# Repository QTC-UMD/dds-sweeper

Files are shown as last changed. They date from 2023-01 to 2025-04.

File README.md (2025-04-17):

# dds-sweeper

Raspberry Pi Pico interface for the AD9959 DDS.

If you use this project, please cite as:

E. Huegler, J. C. Hill, and D. H. Meyer, An agile radio-frequency source using internal sweeps of a direct digital synthesizer,
*Review of Scientific Instruments*, **94**, 094705 (2023)
[https://doi.org/10.1063/5.0163342](https://doi.org/10.1063/5.0163342)

## Specs

- The timing capabilities of the DDS-Sweeper are tied to the number of clock cycles the pico takes to send the next instruction.  

| Table Mode      | 1 Channel | 2 Channel | 3 Channel | 4 Channel |
|-----------------|-----------|-----------|-----------|-----------|
| Single Stepping | 500       | 750       | 1000      | 1250      |
| Sweep Mode      | 1000      | 1500      | 2000      | 2500      |

- At the default Pico Clock frequency of 125 MHz those clock cycle counts correspond to the following times:  

| Table Mode      | 1 Channel | 2 Channel  | 3 Channel  | 4 Channel  |
|-----------------|-----------|------------|------------|------------|
| Single Stepping | 4 $\mu s$ | 6  $\mu s$ | 8  $\mu s$ | 10 $\mu s$ |
| Sweep Mode      | 8 $\mu s$ | 12 $\mu s$ | 16 $\mu s$ | 20 $\mu s$ |

- The number of instructions you can store in the table depends on the type of sweep being performed, the number of channels being used, and the pico chip version. We allocated a maximum ram size of:

244 kB (RP 2040):

| Table Mode                  | 1 Channel | 2 Channel | 3 Channel | 4 Channel |
|-----------------------------|-----------|-----------|-----------|-----------|
| Single Stepping (Ext Timer) | 16656     | 8615      | 5810      | 4383      |
| Sweep Mode (Ext Timer)      | 8614      | 4382      | 2938      | 2210      |
| Single Stepping (Int Timer) | 5000      | 5000      | 5000      | 4032      |
| Sweep Mode (Int Timer)      | 5000      | 4032      | 2703      | 2033      |

500 kB (RP 2350):

| Table Mode                  | 1 Channel | 2 Channel | 3 Channel | 4 Channel |
|-----------------------------|-----------|-----------|-----------|-----------|
| Single Stepping (Ext Timer) | 34132     | 17654     | 11905     | 8981      |
| Sweep Mode (Ext Timer)      | 17654     | 8981      | 6022      | 4529      |
| Single Stepping (Int Timer) | 5000      | 5000      | 5000      | 5000      |
| Sweep Mode (Int Timer)      | 5000      | 5000      | 5000      | 4353      |

## How to flash the firmware

Download the latest [dds-sweeper.uf2 file](https://github.com/QTC-UMD/dds-sweeper/releases/latest/download/dds-sweeper.uf2).
On your Raspberry Pi Pico, hold down the "bootsel" button while plugging the Pico into USB port on a PC (that must already be turned on).
The Pico should mount as a mass storage device (if it doesn't, try again or consult the Pico documentation).
Drag and drop the `.uf2` file into the mounted mass storage device.
The mass storage device should unmount after the copy completes. Your Pico is now running the DDS Sweeper firmware!

## Usage

### Setup

When the DDS Sweeper is started, configuration is required before it can be used. It is often good to begin with a `reset` command, which resets the AD9959.

First, the clock should be setup with the `setclock` command, followed by the `setmult` command.

Second, the number of channels should be configured with the `setchannels` command.

Finally, the mode and timing should be setup with the `mode` command. The DDS Sweeper uses either discrete amplitude, frequency, and phase steps or sweeps of one parameter (possibly with steps of the other parameter) as its primitive instructions. The DDS Sweeper can then use internal timing (in which case it generates triggers internally after each step or sweep) or external timing (in which case it waits for external triggers).

### Program loading

Once setup is complete, instructions (steps or sweeps, depending on the mode) and timings can be loaded using the `set`, `seti`, or `setb` commands. In addition to output instructions, there are special stop and repeat instructions (which can only be loaded using `seti` and `setb`). With instructions are loaded, the address (order in which they are executed) is specified, so the order of loading need not match the order of execution. Timing is set per address, so it is common to all channels. The stop instruction ends program execution, while the repeat instruction restarts program execution from the beginning. Instructions are loaded into an uninitialized array, so skipping instruction addresses or failing to specify stop/repeat at the end of the program may result in undefined behavior.

### Execution

Finally, the program can be executed using the `start` or `hwstart` commands. If termination of the program is required before it reaches a `stop` command, the `abort` command can be used.

## DDS Units

- Output Amplitude is dependent on frequency (some people on Analog Devices forum mentioned amplitude and frequency are related by a sinc function)

- The frequency resolution of the AD9959 is $= \frac{f_{sys clk}}{2^{32}}$. At the default system clock of 500 MHz, the frequency resolution is $\approx 0.1164$ Hz. Frequency input to the DDS Sweeper using the `set` command will be rounded to an integer multiple of the frequency resolution. Frequency input to the DDS Sweeper using the `seti` or `setb` commands will be in units of the frequency resolution.

- The phase resolution of the AD9959 is $= \frac{360^\circ}{2^{14}} \approx 0.02197^\circ$. Phase offsets given using the `set` command will be rounded to a multiple of this resolution. Phase offsets given using the `seti` or `setb` commands will be in units of this resolution.

- The amplitude resolution of the AD9959 is $= \frac{1}{2^{10}} \approx 0.09767\%$. Amplitude scale factors given using the `set` command will be rounded to a multiple of this resolution. Amplitude scale factors given using the `seti` or `setb` commands will be in units of this resolution.

- When the DDS Sweeper uses internal timing to execute instructions, that time is based on the number of clock cycles of the Pico's system clock (which defaults to 125 MHz for an 8 ns period). Timing inputs using the `set` command are given in seconds and will be rounded to an integer multiple of the Pico system clock period. Timing input using the `seti` or `setb` commands is defined to be in units of the Pico system clock period.

## Sweeps

- Setting up a sweep:  
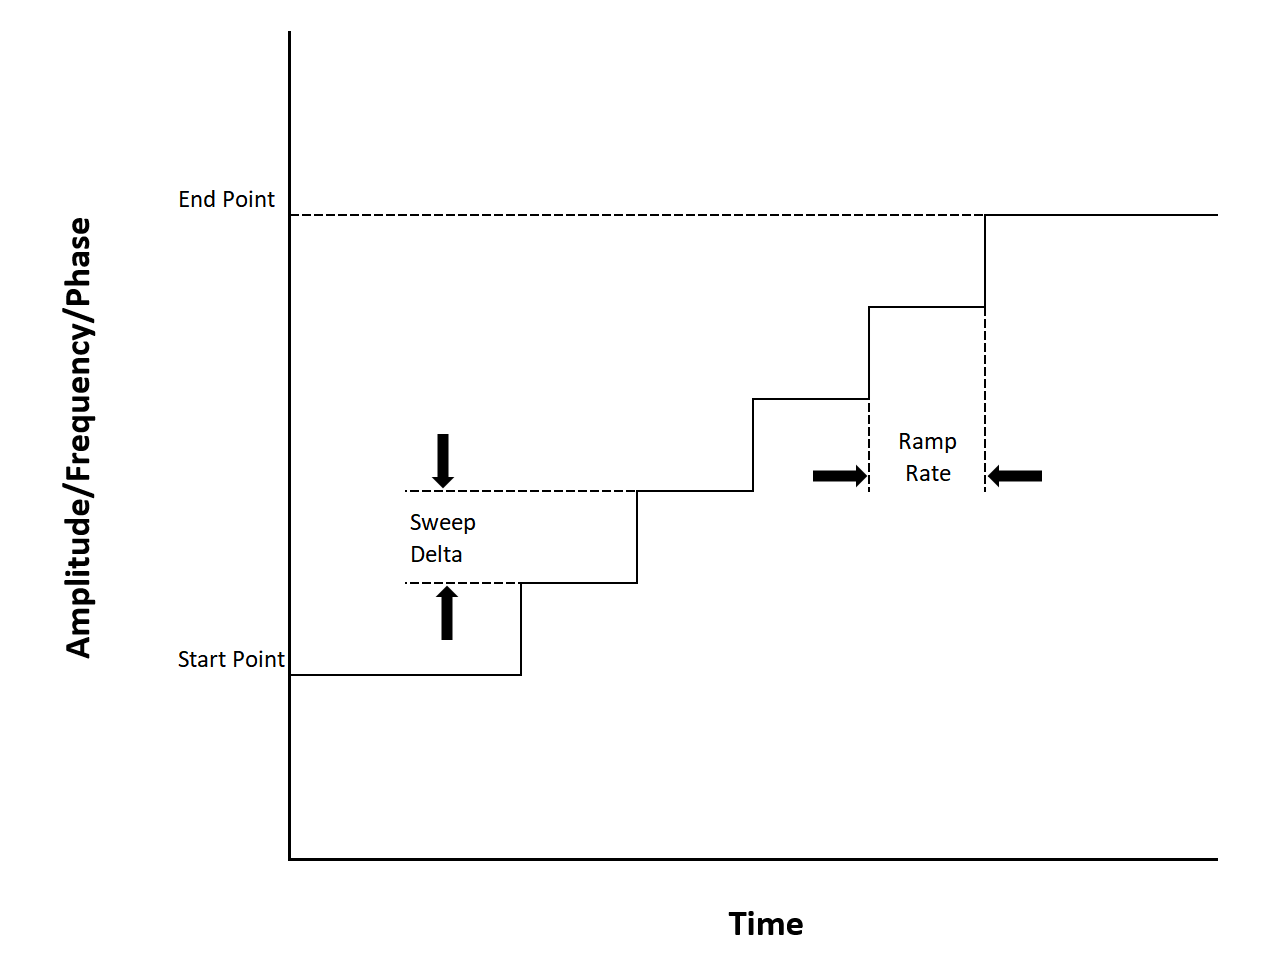
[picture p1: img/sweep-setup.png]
Sweep Setup Figure
  
Sweeps are defined by two parameters, sweep delta and ramp rate.
- Sweep Delta defines the change in output amplitude/frequency/phase on each sweep step
- Ramp rate defines how often a sweep step is taken. It is based off of the AD9959's sync clock signal which will be one quarter of the AD9959's system clock. The ramp rate parameter specifies the number of sync clock cycles per sweep step. A ramp rate of 1 will cause the sweep delta to be applied every 1 sync clock cycle. For upward sweeps, the ramp rate parameter can have a value of 1-255. For downward sweeps the ramp rate can only be 1.  

For more details on sweeps, see [sweep details](SWEEP_DETAILS.md).

## Serial API

Note: Commands must be terminated with `\n`.

### Status commands

- `version`:  
Responds with a string containing the firmware version.

- `status`:  
Returns the operating status of the DDS-Sweeper.

  - `0`: manual mode
  - `1`: transitioning to buffered execution
  - `2`: buffered execution
  - `3`: aborting buffered execution
  - `4`: last buffered execution was aborted
  - `5`: transitioning to manual mode

- `clkstatus`:
Returns the clocking status of the DDS-Sweeper as three numbers: `<int:mode> <double:freq> <int:mult>`.
Mode can be `0` for internal clocking or `1` for external clocking of the AD9959.
The frequency is the AD9959 reference frequency, in Hz.
`mult` is the AD9959 PLL multiplier. The corresponding system frequency is `freq*-*mult`.

- `board`:
Responds with which type of board the firmware is running on: `pico1` or `pico2`.

- `getfreqs`:  
Responds with a multi-line string containing the current operating frequencies of various clocks (you will be most interested in `pll_sys` and `clk_sys`). Multiline string ends with `ok\n`.

### State commands

- `start`:  
Starts buffered execution immediately.

- `hwstart`:  
Starts buffered execution once an external trigger is received.

- `abort`:  
Stops buffered execution immediately.

### Setup commands

- `setclock <mode:int> <freq:int> (<pll_mult:int>)`:  
Reconfigures the source/reference clock.
  - Mode `0`: Use pico system clock as reference to the AD9959.
    In this mode, the frequency provided also sets the pico system clock
    and it cannot exceed 133 MHz.
    The dds sweeper defaults to this mode with a frequency of 125 MHz and a PLL multiplier of 4.
  - Mode `1`: Sets the AD9959 to receive a reference clock not from the pico.
    Setting this mode does not change the pico system clock.

  `pll_mult` is an optional input that sets the AD9959's PLL multiplier on the Reference Clock input. The default value is 4, giving the AD9959 a system clock of 500 MHz with the pico's 125 MHz reference. Valid values are 1 or 4-20.  
  The AD9959's PLL has an output range of 100-160 MHz or 255-500 MHz with VCO gain enabled. The pico will automatically enable the VCO gain bit if the requested frequency is in the upper range. If trying to use the PLL multiplier to generate a frequency between 160 and 255 MHz, there is no guarantee of operation.

- `setchannels <num:int>`:  
Sets how many channels being used by the table mode. Uses the lowest channels first, starting with channel 0. If number of channels is set to `0`, buffered execution instructions will be written to all 4 channels simultaneously.

- `mode <sweep-type:int> <trigger-source:int>`:  
Configures what mode the DDS-Sweeper is operating in
  - 0: single stepping / manual mode
  - 1: amplitude sweep
  - 2: frequency sweep
  - 3: phase sweep
  - 4: amplitude sweep with frequency/phase steps
  - 5: frequency sweep with amplitude/phase steps
  - 6: phase sweep with frequency/amplitude steps  

  The operating mode must be set before buffered execution instructions can be programmed into the DDS-Sweeper.  
  A `trigger-source` of `0` means the Sweeper is expecting external triggers. A `trigger-source` of `1` means the Sweeper will send its own triggers and `set` commands will require an additional `time` argument.

### Manual output commands

- `setfreq <channel:int> <frequency:float>`:  
Manually set the output frequency of a specified channel. Channels are 0-3 and frequencies are in Hz. If `debug` is set to on, it will respond with the actual frequency set. The Sweeper must be in manual mode.

- `setphase <channel:int> <phase_offset:float>`:  
Manually set the phase offset of a specified channel. Channels are 0-3 and offsets are in degrees. If `debug` is set to on, it will respond with the actual degree offset set. The Sweeper must be in manual mode.

- `setamp <channel:int> <amplitude_scale_factor:float>`:  
Manually set the amplitude scale factor of a specified channel. Channels are 0-3 and amplitude scale factors are a precentage of the maximum output voltage. If `debug` is set to on, it will respond with the actual frequency set. The Sweeper must be in manual mode.

### Data loading commands

- `set`:  
Sets the value of instruction number `addr` for channel `channel` (zero indexed). `addr` starts at 0. It looks different depending on what mode the sweeper is in. If `Debug` is set to `on` it will respond with the actual values set for that instruction.
  - Single Stepping (mode 0): `set <channel:int> <addr:int> <frequency:float> <amplitude:float> <phase:float> (<time:float>)`
  - Sweep Mode (modes 1-3): `set <channel:int> <addr:int> <start_point:float> <end_point:float> <sweep_rate:float> (<time:float>)`

    `start_point` is the value the sweep should start from, and `end_point` is where it will stop. `sweep_rate` is the amount that the output should change in each quantity's units per second (further info below). In the AD9959, the sweep clock runs at one quarter the system clock. The types of values expected for `start_point`, `end_point`, and `sweep_rate` are different depending on the type of sweep:  
    - Amplitude Sweeps (mode 1)  
      `start_point` and `end_point` should be decimals between 0 and 1 that represent the desired proportion of the maximum output amplitude. `sweep_rate` is then that proportion per second. The resolution of the start and end values is $\frac{1}{1024} \approx 0.09766$.
    - Frequency Sweeps (mode 2)  
      `start_point` and `end_point` are frequencies in Hz, with `sweep_rate` in Hz per second. The start and end points can have decimal values, but they will be rounded to the nearest multiple of the frequency resolution ($\frac{f_{sysclk}}{2^{32}}$).
    - Phase Sweeps (mode 3)
      `start_point`, `end_point` are in degrees, with `sweep_rate` in degrees per second. The start and end points can have decimal values, but they will be rounded to the nearest multiple of the phase resolution ($\frac{360^\circ}{2^{14}} \approx 0.02197^\circ$).

  - Sweep and Single Stepping Mode (modes 4-6): `set <channel:int> <addr:int> <start_point:float> <end_point:float> <sweep_rate:float> <secondary1:double> <secondary2:double> (<time:float>)`

  These modes perform a linear sweep on one of the parameters, while simultaneously single stepping on the other two parameters.
  - Amplitude Sweeps (mode 4)  
    `secondary1` is the frequency, and `secondary2` is the phase offset.
  - Frequency Sweeps (mode 5)  
    `secondary1` is the amplitude scale factor, and `secondary2` is the phase offset.
  - Phase Sweeps (mode 6)  
    `secondary1` is the frequency, and `secondary2` is the amplitude scale factor.

- `seti`:  
Sets the value of instruction number `addr` for channel `channel` (zero indexed). `addr` starts at 0. It looks different depending on what mode the sweeper is in. If `Debug` is set to `on` it will respond with the actual values set for that instruction. `seti` uses integer values (AD9959 units) rather than floating point values. Otherwise, it is the same as `set`.
  - Single Stepping (mode 0): `seti <channel:int> <addr:int> <frequency:int> <amplitude:int> <phase:int> (<time:int>)`
  - Sweep Mode (modes 1-3): `seti <channel:int> <addr:int> <start_point:int> <end_point:int> <delta:int> <ramp-rate:int> (<time:int>)`

    `start_point` is the value the sweep should start from, and `end_point` is where it will stop. `delta` is the amount that the output should change by every cycle of the sweep clock. In the AD9959, the sweep clock runs at one quarter the system clock. `ramp-rate` is an additional divider that can applied to slow down the sweep clock further, must be in the range 1-255. The types of values expected for `start_point`, `end_point`, and `delta` different depending on the type of sweep  
    - Amplitude Sweeps (mode 1)  
      `start_point` and `end_point` should be integers between 0 and 1023 (inclusive).
    - Frequency Sweeps (mode 2)  
      `start_point`, `end_point`, and `delta` are integers between 0 and $2^{32} - 1$ in units of system clock rate (typically $500$ MHz) over $2^{32}$.
    - Phase Sweeps (mode 3)
      `start_point`, `end_point`, and `delta` are between 0 and 65535 (inclusive).

  - Sweep and Single Stepping Mode (modes 4-6): `set <channel:int> <addr:int> <start_point:int> <end_point:int> <delta:int> <ramp-rate:int> <secondary1:int> <secondary2:int> (<time:int>)`

    These modes perform a linear sweep on one of the parameters, while simultaneously single stepping on the other two parameters.
    - Amplitude Sweeps (mode 4)  
      `secondary1` is the frequency, and `secondary2` is the phase offset.
    - Frequency Sweeps (mode 5)  
      `secondary1` is the amplitude scale factor, and `secondary2` is the phase offset.
    - Phase Sweeps (mode 6)  
      `secondary1` is the frequency, and `secondary2` is the amplitude scale factor.

- `setb <start address:int> <instruction count:int>`:  
Bulk setting of instructions in binary. `start address` is the address of the first instruction loaded. `instruction count` instructions will be programmed. If there is not sufficient space for that many instructions, the response will be an error message. Otherwise, the response will be `ready for <byte count:int> bytes`, where `byte count` is the number of bytes the device is expecting. An array of instructions can then be transmitted. Note that all active channels are loaded together. The layout of the instruction array is mode dependent, and in the table below each mode is assumed to use external timing (where internal timing bytes are in parentheses and the dtype list must have `, ('time', '<u4')` appended)

| Mode  | Bytes per channel per instruction  | np.dtype  |
|---| :---: |:---:|
| Single Stepping (mode 0)  | 8 (12) | `[('frequency', '<u4'), ('amplitude', '<u2'), ('phase', '<u2')]`  |
| Amplitude Sweeps (mode 1)  | 7 (11) |  `[('start_amplitude', '<u2'), ('stop_amplitude', '<u2'), ('delta', '<u2'), ('rate', '<u1')]` |
| Frequency Sweeps (mode 2) | 13 (17) |  `[('start_frequency', '<u4'), ('stop_frequency', '<u4'), ('delta', '<u4'), ('rate', '<u1')]` |
| Phase Sweeps (mode 3)  | 7 (11) | `[('start_phase', '<u2'), ('stop_phase', '<u2'), ('delta', '<u2'), ('rate', '<u1')]` |
| Amplitude Sweep and Single Stepping (mode 4) | 13 (17)  | `[('start_amplitude', '<u2'), ('stop_amplitude', '<u2'), ('delta', '<u2'), ('rate', '<u1'), ('frequency', '<u4'), ('phase', '<u2')]`  |
| Frequency Sweep and Single Stepping (mode 5) | 17 (21) | `[('start_frequency', '<u4'), ('stop_frequency', '<u4'), ('delta', '<u4'), ('rate', '<u1'), ('amplitude', '<u2'), ('phase', '<u2')]`  |
| Phase Sweep and Single Stepping (mode 6)  | 13 (17) | `[('start_phase', '<u2'), ('stop_phase', '<u2'), ('delta', '<u2'), ('rate', '<u1'), ('frequency', '<u4'), ('amplitude', '<u2')]`  |

### Flash commands

- `save`:  
Saves the buffered execution table to nonvolatile memory so that it can be recovered later (after a power cycle).

- `load`:  
Retrieves the buffered execution table stored in nonvolatile memory and restores it to system memory so that it can be run. A saved table must be loaded before it can be run.

### Debugging commands

- `debug <state:str>`:  
Turns on extra debug messages printed over serial. `state` should be `on` or `off` (no string quotes required). On by default.

- `numtriggers`:  
Responds with the number of triggers processed since the last call of `start`

- `program`:  
Reboots the Pi Pico into firmware flashing mode. Serial will immediately disconnect and a mass storage device should appear.

## Compiling the firmware

If you want to make changes to the firmware, or want to compile it yourself (because you don't trust binary blobs from the internet), we provide a docker configuration to help you do that.

1. Install docker desktop and make sure it is running (if you are on Windows, you may have to mess around a bit to get virtualisation working at an operating system level)
2. Clone this repository
3. Open a terminal with the current working directory set to the repository root (the `docker-compose.yaml`` file should be there)
4. Run `docker compose build --pull` to build the docker container
5. Run `docker compose up` to build the PrawnBlaster firmware.

Step 4 will take a while as it has to build the docker container.
If it is slow to download packages from the Ubuntu package repositories, consider providing an explicit apt mirror that is fast for you: `docker compose build --pull --build-arg APT_MIRROR="http://azure.archive.ubuntu.com/ubuntu/"`.

If you want to change which version of the pico SDK it builds against, this is set in the `build/docker/Dockerfile` file.
Just change the git tag of the pico SDK that gets cloned out by git, then rebuild the docker container (see step 4).

Note once the docker container is built, you can run step 5 as many times as you like.
You do not need to rebuild the container, even if you make changes to the PrawnBlaster source code.
You only need to rebuild the docker container if you modify the `build/docker/Dockerfile` file.

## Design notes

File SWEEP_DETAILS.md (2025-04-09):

# Sweeps

- Setting up a sweep:  
Sweep Setup Figure  
Sweeps are defined by two parameters, sweep delta and ramp rate.
- Sweep Delta defines the change in output amplitude/frequency/phase on each sweep step.
- Ramp rate defines how often a sweep step is taken. It is based off of the AD9959's sync clock signal which will be one quarter of the AD9959's system clock. The ramp rate parameter specifies the number of sync clock cycles per sweep step. A ramp rate of 1 will cause the sweep delta to be applied every 1 sync clock cycle. For upward sweeps, the ramp rate parameter can have a value of 1-255. For downward sweeps the ramp rate can only be 1.  

The time between sweep steps can be calculated with:
$ t = \frac{\textrm{Ramp Rate}}{\textrm{Sync Clock}} $
Using the Pico's 125 Mhz with a 4 times PLL Multiplier gives the AD9959 a system clock of 500 MHz and therefore a sync clock of 125 MHz.
For upward sweeps the time between sweeps can range from $\frac{1}{125 MHz} = 8 ns$ to $\frac{255}{125 MHz} = 2.04 \mu s$.
Downward sweeps will apply the sweep delta every $\frac{1}{125 MHz} = 8 ns$.  
Given the frequency resolution of $\frac{f_{sys clk}}{2^{32}}$, the smallest sweep delta is $\frac{1}{2^{32}} = 0.1164$ Hz. With the maximum ramp rates, the DDS-sweeper has a minimum sweeping rate of $\approx 47871$ Hz/sec when sweeping upwards or $\approx 12207031.25$ Hz/sec when sweeping downward.

## Finer Sweep Rate Resolution in `set`

The `set` command will internally calculate the sweep delta and ramp rate by given the user provided `sweep_rate` using the continued fraction algorithm. Given a conversion factor $B$ that allows us to convert a sweep rate $R$ to bits per sync clock cycle,  

$$B_{freq} = \frac{2^{32}}{f_{sysclk}} [\frac{\text{bits}}{\text{Hz}}], B_{amp} = 2^{10} [\frac{\text{bits}}{\text{Arb.}}], B_{phase} = 2^{14}[\frac{\text{bits}}{\text{degree}}],$$

the ratio of sweep delta $d$ and ramp rate $r$ can be equated to the following:  

$$
\frac{d}{r} = B\frac{4R}{f_{sysclk}}
$$.

The continued fraction algorithm then returns the integer ratio approximation of the desired `sweep_rate` float and therefore set an integer sweep delta and ramp rate. The algorithm will respect the limits of each sweep mode, so the frequency tuning word sweep deltas can be between $0$ and $2^{32}-1$, amplitude scale factor sweep deltas can be between $0$ and $2^{10}$, and phase offset word sweep deltas can be between $0$ and $2^{14}$. The ramp rates for each mode are constrained to be between $1$ and $255$ for upward sweeps, and held to $1$ for downward sweeps.

## Downward Sweeps

Downward sweeps are not well supported by the AD9959, but they can still be done.
The best method I have found for doing a downward sweep is to send the instructions via serial first, with the sweep autoclear bit set to active and the rising sweep tuning word set to the maximum.
Then issue the IO_UPDATE signal while keeping the profile pin for that channel high.
I believe this clears the sweep accumulator then quickly refills it with a max rate sweep before beginning the downward sweep.
Other combinations of autoclear bit active or not and timing of the profile pins seem to cause even more issues with downward sweeps.
The biggest downside of this method is that you cannot slow down the downward sweep ramp rate as much as the upward sweep ramp rate.

- Autoclear Accumulator Active, drop the pin after the update:  
  Seems to work, you just cannot slow down downward sweeps.
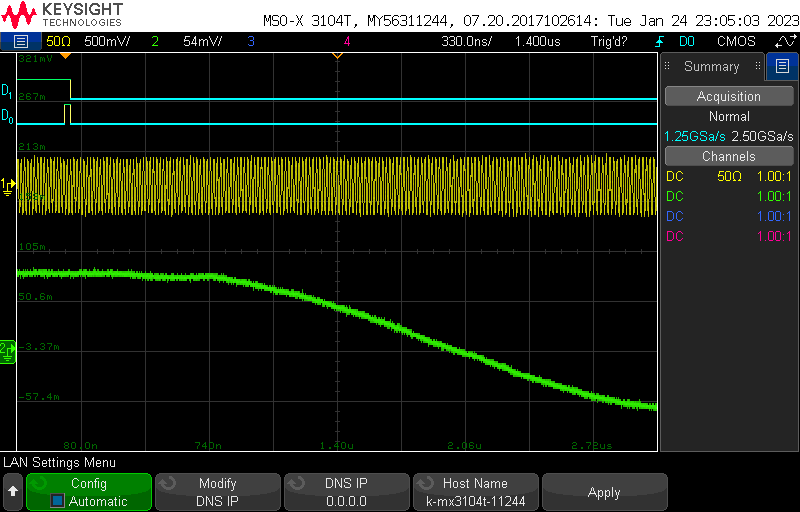
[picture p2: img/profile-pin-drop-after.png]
Autoclear Accumulator Active, drop the pin after the update Closeup
    
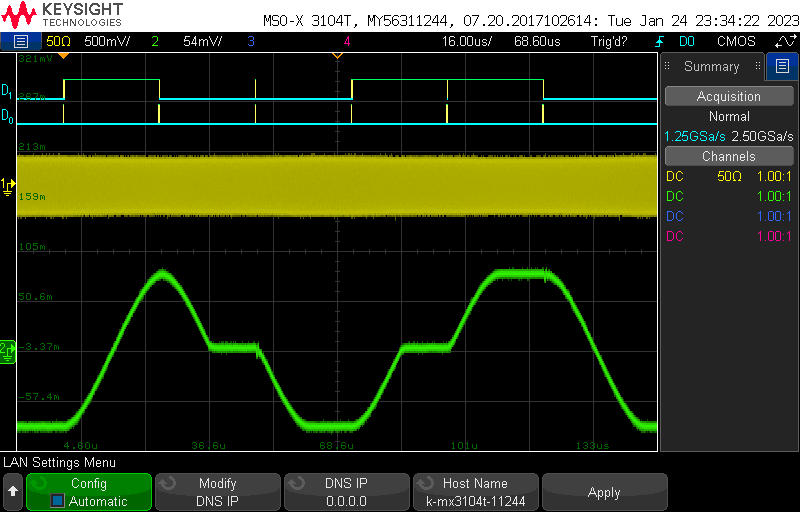
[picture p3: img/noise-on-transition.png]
Autoclear Accumulator Active, drop the pin after the update Multiple Sweeps
  

- Autoclear Accumulator Active, drop the pin before the update:  
  Downward sweeps just dont work at all.  
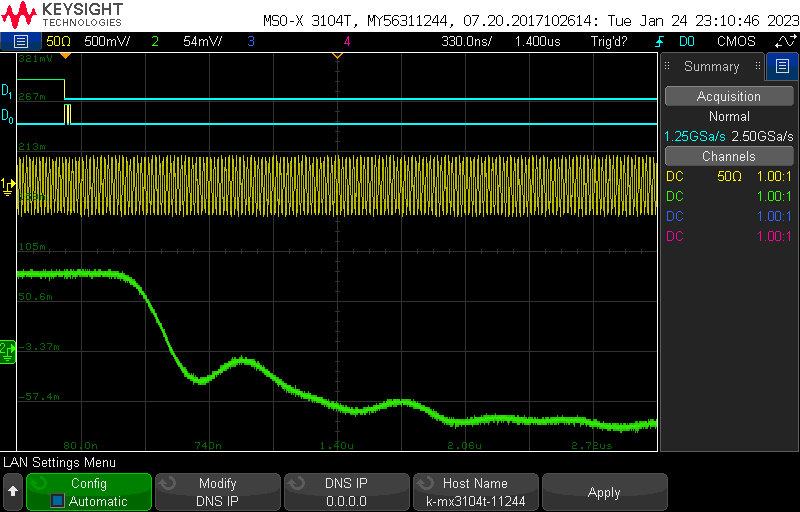
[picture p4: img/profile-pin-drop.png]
Autoclear Accumulator Active, drop the pin before the update: Closeup
    
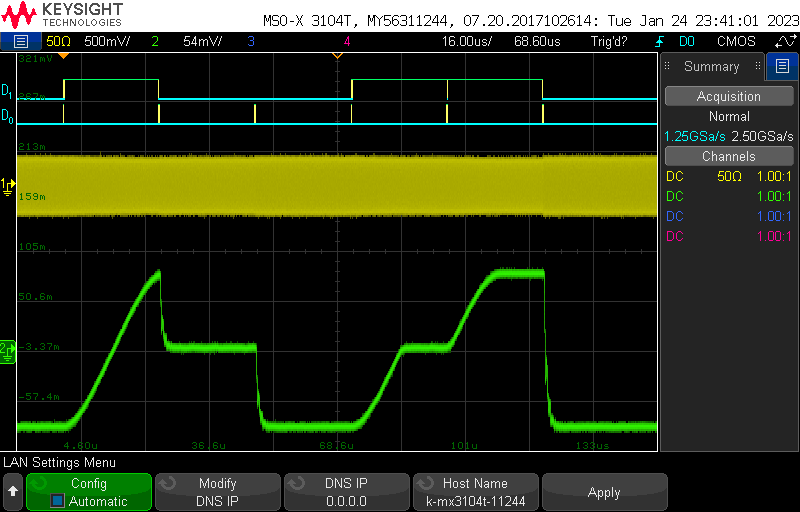
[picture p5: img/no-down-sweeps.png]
Autoclear Accumulator Active, drop the pin before the update: Multiple Sweeps
    

- no autoclear, drop pin before update:  
  You cannot do consecutive down sweeps - every down sweep must be preceeded by an up sweep  
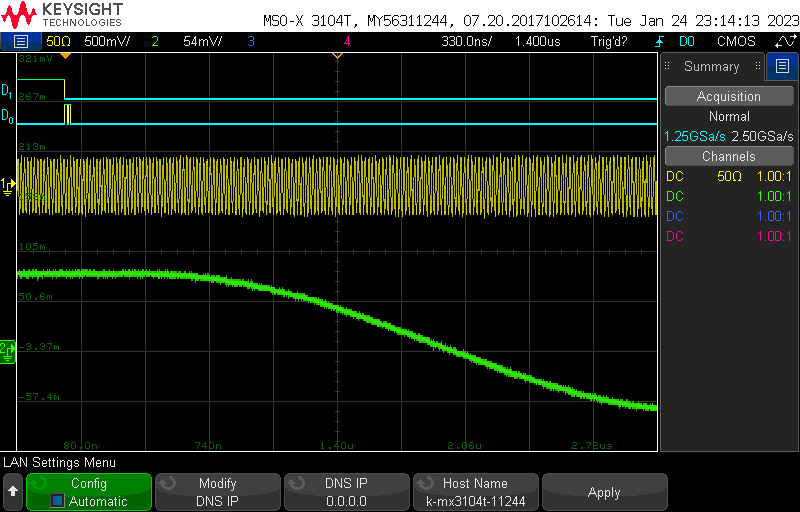
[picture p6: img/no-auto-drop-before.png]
no autoclear, drop pin before update: Closeup
    
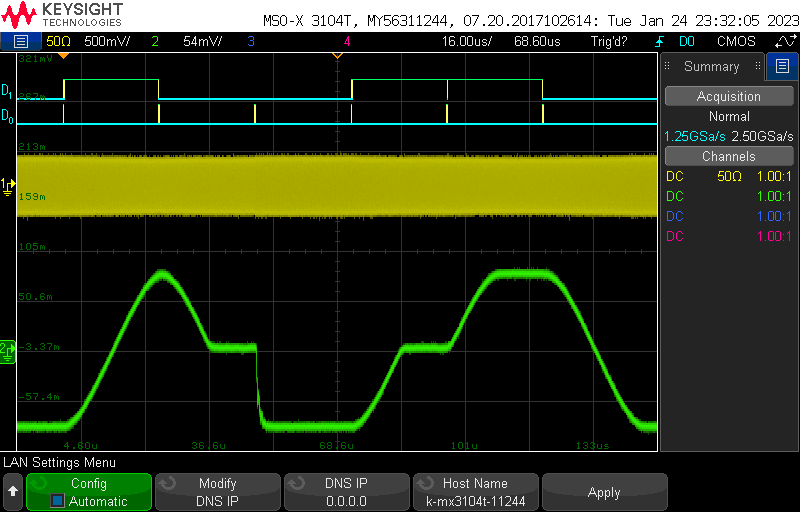
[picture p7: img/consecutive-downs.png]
no autoclear, drop pin before update: Multiple Sweeps
    

- no autoclear, drop pin after update:
  A down sweep after an up sweep cannot cover a greater distance than the upward sweep  
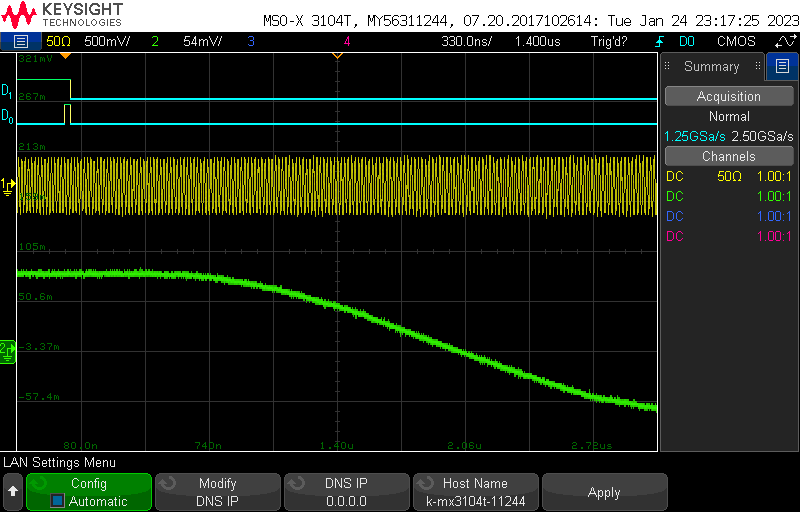
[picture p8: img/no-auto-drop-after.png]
no autoclear, drop pin after update: Closeup
    
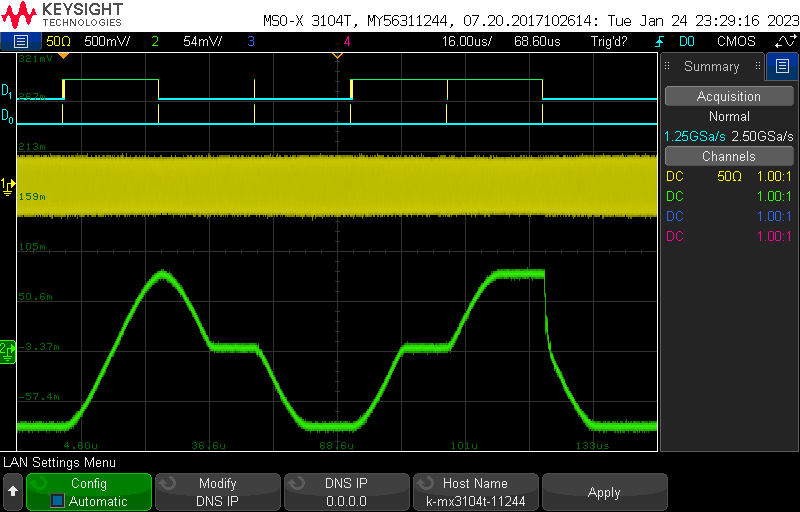
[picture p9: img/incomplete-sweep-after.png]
no autoclear, drop pin after update: Multiple Sweeps
    

- You can also generate a downward sweep by operating the AS9959 above the nyquist frequency.
This method does work but causes discontinuity when switching which band the AD9959 is working in.  
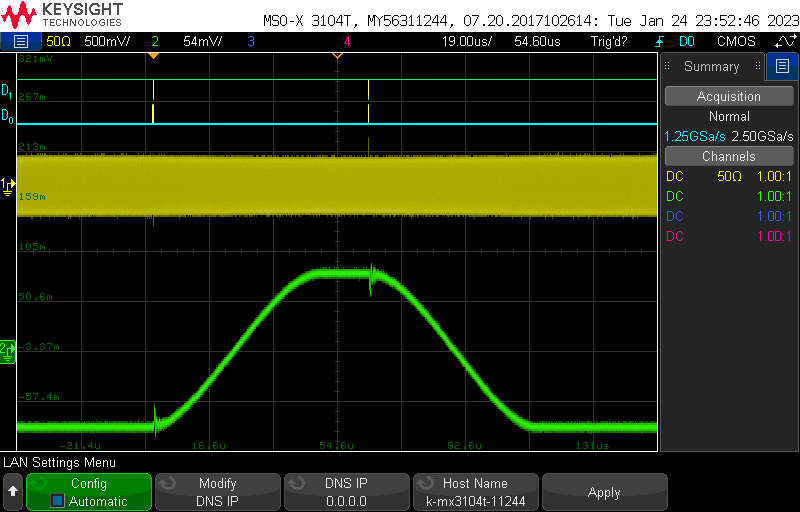
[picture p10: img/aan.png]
Scope trace of noise on DDS band transitions


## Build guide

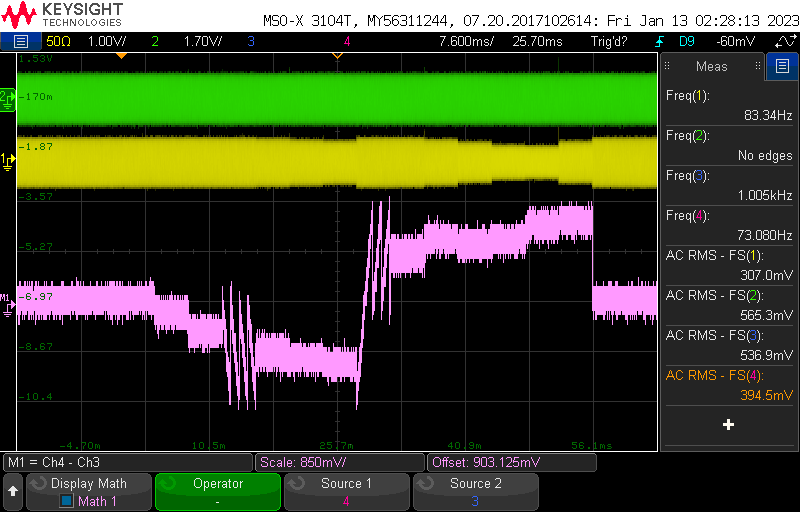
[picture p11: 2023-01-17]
img/pfd-many-steps.png

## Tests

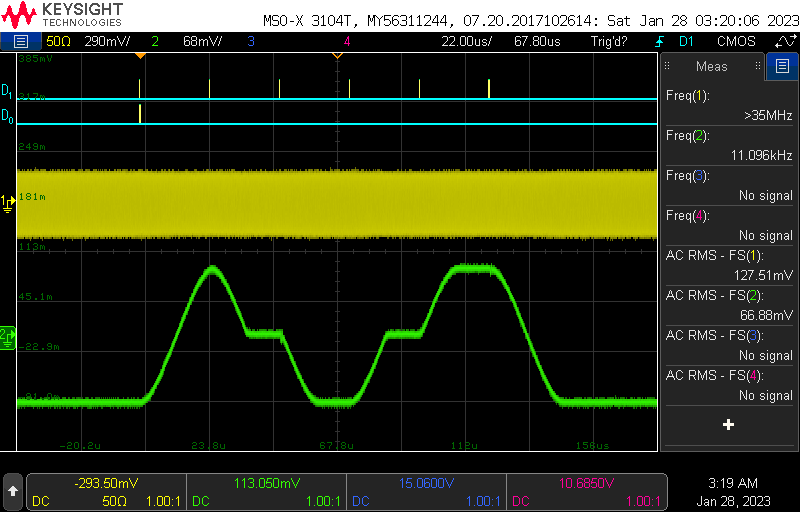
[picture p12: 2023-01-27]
img/freq-test.png

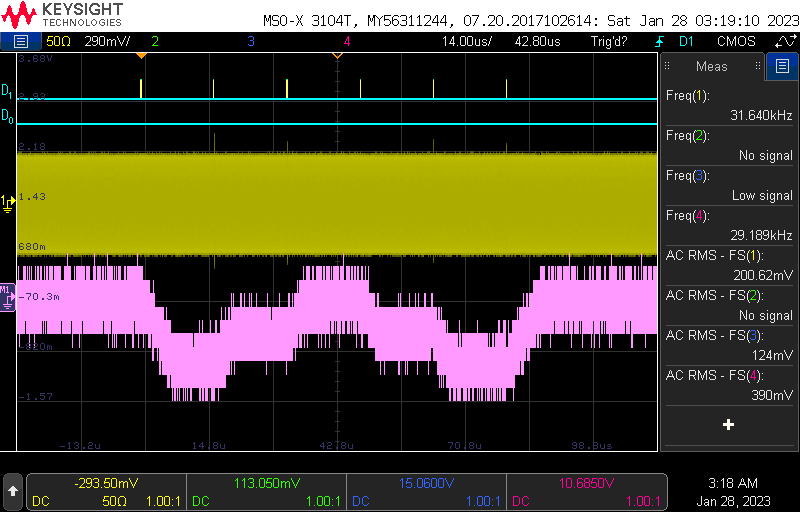
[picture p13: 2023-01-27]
img/phase-test.png

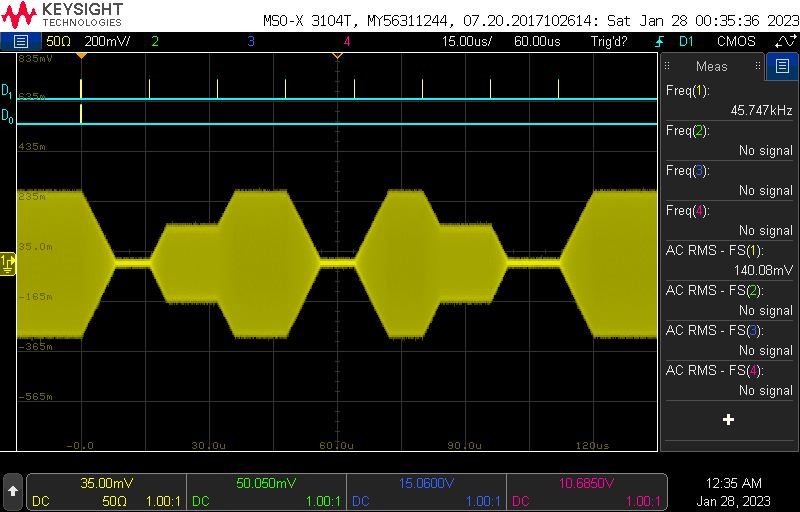
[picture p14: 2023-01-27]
img/amp-test.png

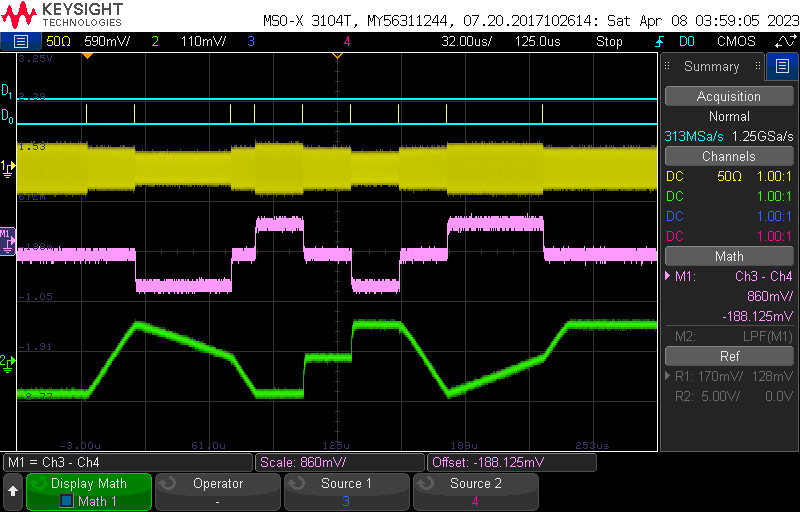
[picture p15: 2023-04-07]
testing/all_sweep.png

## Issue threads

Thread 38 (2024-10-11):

### ISSUE TITLE
Pin Layout Issue

### ISSUE THREAD

**Issue by ehuegler** [QTC-UMD/dds-sweeper#38]
There is a memory misalignment issue which can cause the DDS to go into an unrecoverable error state. The current iteration of the board does not have any connection between the pico and the AD9959 reset pin that would reset the DDS, so the only way to recover is to power cycle the both the pico and the AD9959.

I did fix this problem by soldering an additional wire onto the boards. The problem is that to actually incorporate this wire as a trace on the breakout board is to switch the two of the GPIO pins the pico is currently using which can be done easily in the firmware.

Basically the problem can be trivially fixed but it would break the two working boards I have. For now these boards are still necessary to keep on testing. When I have a chance I just need to make new boards to replace them so that I can push the change to the repo.

**Comment by dihm** [comment]
Whenever one of us gets to this, it would be good to further widen some of those small traces winding around the Pico. We went to print another test board based on the files in the repo and they were still going to mill a bit too small.

**Comment by dihm** [comment]
This was fixed in #39

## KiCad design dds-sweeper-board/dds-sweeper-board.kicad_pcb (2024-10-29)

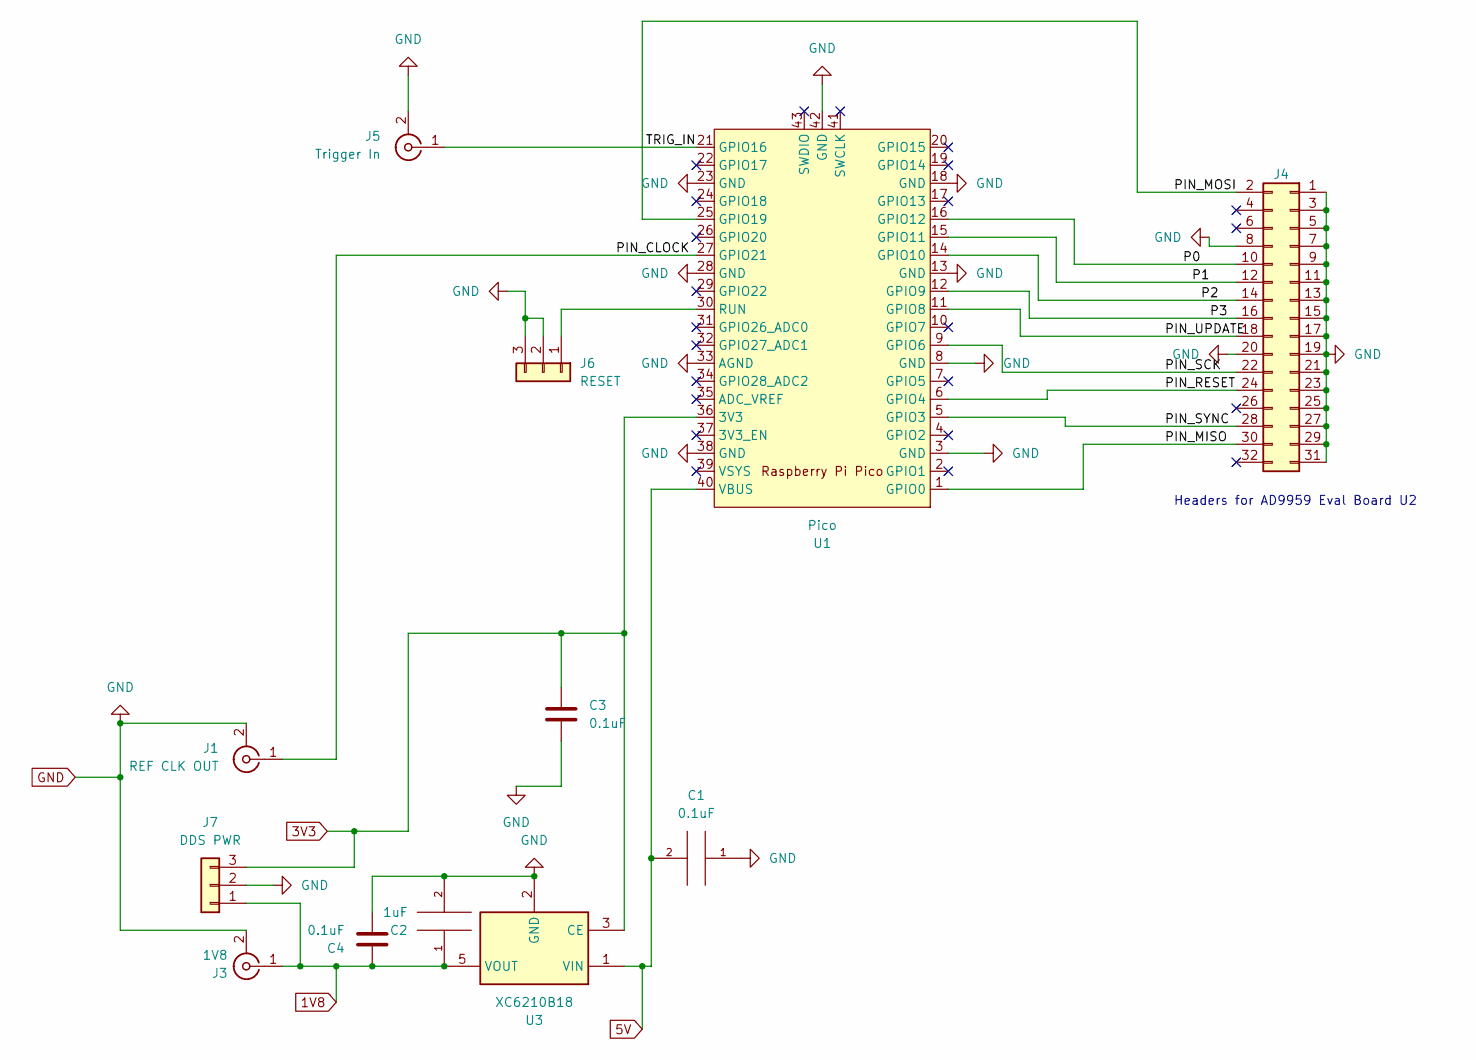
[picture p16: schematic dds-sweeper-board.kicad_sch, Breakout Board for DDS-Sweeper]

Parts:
C1, C3, C4: 0.1uF; C_0805_2012Metric_Pad1.18x1.45mm_HandSolder
C2: 1uF; C_0805_2012Metric_Pad1.18x1.45mm_HandSolder
J1: REF CLK OUT; SMA_Samtec_SMA-J-P-X-ST-EM1_EdgeMount
J3: 1V8; SMA_Samtec_SMA-J-P-X-ST-EM1_EdgeMount
J4: AD9959 Eval Header; PinSocket_2x16_P2.54mm_Vertical
J5: Trigger In; SMA_Samtec_SMA-J-P-X-ST-EM1_EdgeMount
J6: RESET; PinSocket_1x03_P2.54mm_Vertical
J7: DDS PWR; PinSocket_1x03_P2.54mm_Vertical
U1: Pico; RPi_Pico_SMD
U3: XC6210B18; SOT-23-5

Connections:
1V8: C2.1, C4.1, J3.1 (In), J7.1, U3.5 (VOUT)
3V3: C3.2, J7.3, U1.36 (3V3), U3.3 (CE)
5V: C1.2, U1.40 (VBUS), U3.1 (VIN)
/P0: J4.10, U1.16 (GPIO12)
/P1: J4.12, U1.15 (GPIO11)
/P2: J4.14, U1.14 (GPIO10)
/P3: J4.16, U1.12 (GPIO9)
/PIN_CLOCK: J1.1 (In), U1.27 (GPIO21)
/PIN_MISO: J4.30, U1.1 (GPIO0)
/PIN_MOSI: J4.2, U1.25 (GPIO19)
/PIN_RESET: J4.24, U1.6 (GPIO4)
/PIN_SCK: J4.22, U1.9 (GPIO6)
/PIN_SYNC: J4.28, U1.5 (GPIO3)
/PIN_UPDATE: J4.18, U1.11 (GPIO8)
/TRIG_IN: J5.1 (In), U1.21 (GPIO16)
GND: C1.1, C2.2, C3.1, C4.2, J1.2 (Ext), J3.2 (Ext), J4.1, J4.3, J4.5, J4.7, J4.8, J4.9, J4.11, J4.13, J4.15, J4.17, J4.19, J4.20, J4.21, J4.23, J4.25, J4.27, J4.29, J4.31, J5.2 (Ext), J6.2, J6.3, J7.2, U1.3 (GND), U1.8 (GND), U1.13 (GND), U1.18 (GND), U1.23 (GND), U1.28 (GND), U1.33 (AGND), U1.38 (GND), U1.42 (GND), U3.2 (GND)
unnamed: J6.1, U1.30 (RUN)

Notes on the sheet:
Headers for AD9959 Eval Board U2

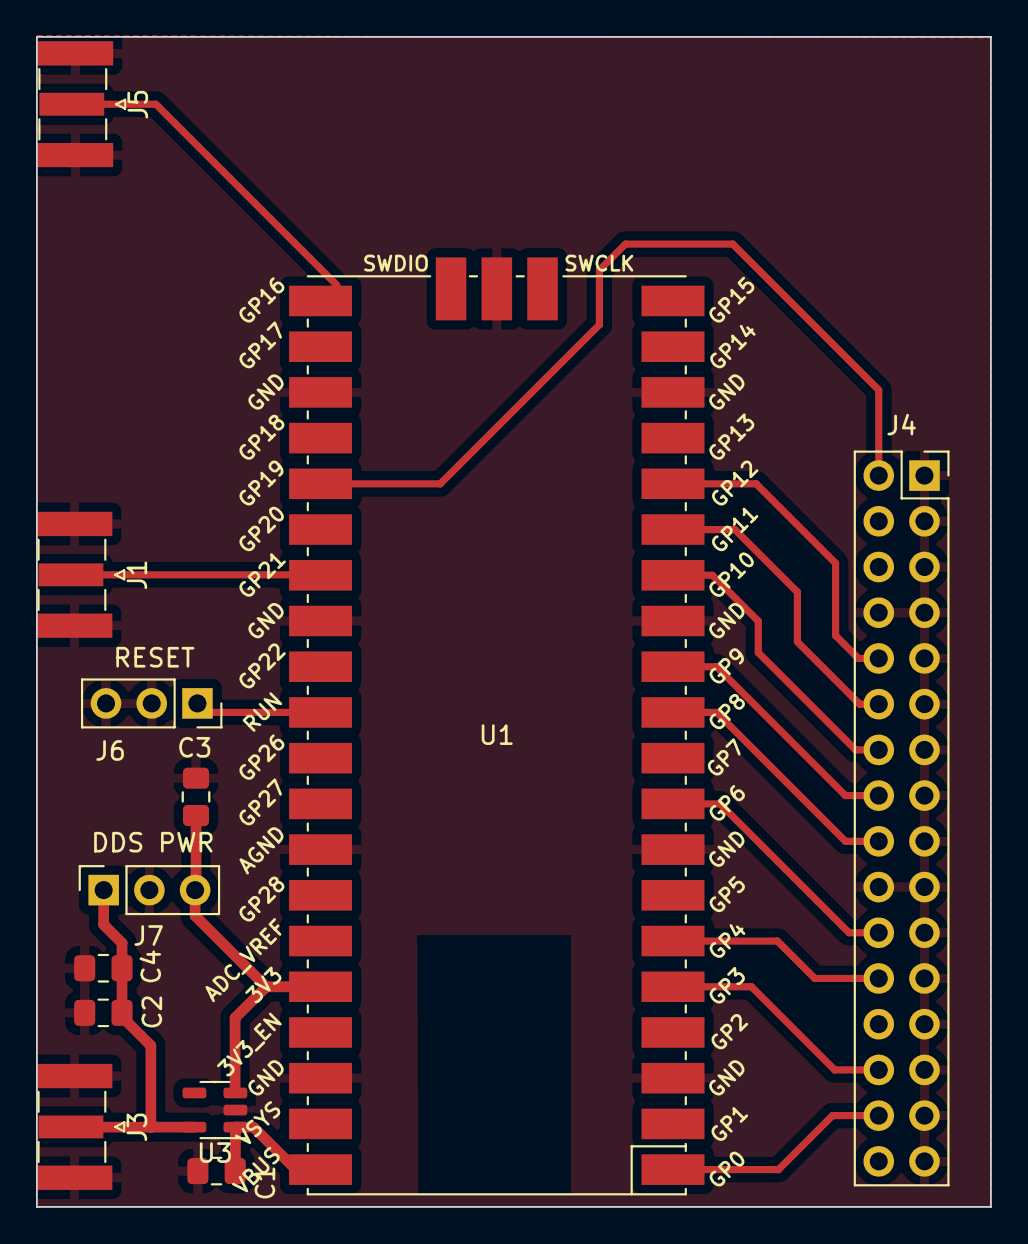
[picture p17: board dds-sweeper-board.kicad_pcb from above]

Board: 2 copper layers, 53.0 x 65.0 mm, 12 parts (0 on the bottom side), 17 nets.

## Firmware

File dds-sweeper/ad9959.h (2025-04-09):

#ifndef _AD9959_H
#define _AD9959_H

#include <math.h>
#include <stdio.h>
#include <string.h>

#include "hardware/clocks.h"
#include "hardware/spi.h"
#include "hardware/structs/watchdog.h"
#include "pico/stdlib.h"

// Default Pins to use
#define PIN_MISO 0  //RX
#define PIN_MOSI 19  //TX
#define PIN_SCK 6
#define PIN_SYNC 3
#define PIN_CLOCK 21
#define PIN_UPDATE 8
#define PIN_RESET 4
#define P0 12
#define P1 11
#define P2 10
#define P3 9
#define PROFILE_ASC false
#define TRIGGER 16
#define INT_TRIGGER 17

#define PIO_TRIG pio0
#define PIO_TIME pio1

#define SPI spi0

// AD9959 registers
#define AD9959_REG_CSR 0x00
#define AD9959_REG_FR1 0x01
#define AD9959_REG_FR2 0x02
#define AD9959_REG_CFR 0x03
#define AD9959_REG_FTW 0x04
#define AD9959_REG_POW 0x05
#define AD9959_REG_ACR 0x06
#define AD9959_REG_LSRR 0x07
#define AD9959_REG_RDW 0x08
#define AD9959_REG_FDW 0x09
#define AD9959_REG_CW 0x0A

// Instruction memory maps
// Defines offset in instruction array where register address is stored
// Register value starts at offset of address
#define INS_CSR 0
// For Single Step
#define INS_SS_FTW 2
#define INS_SS_POW 7
#define INS_SS_ACR 10
// For AMP/AMP2 sweep
#define INS_AMP_ACR 2
#define INS_AMP_LSRR 6
#define INS_AMP_RDW 9
#define INS_AMP_FDW 14
#define INS_AMP_CW 19
#define INS_AMP_CFR 24
#define INS_AMP_FTW 28
#define INS_AMP_POW 33
// For FREQ/FREQ2 sweep
#define INS_FREQ_FTW 2
#define INS_FREQ_LSRR 7
#define INS_FREQ_RDW 10
#define INS_FREQ_FDW 15
#define INS_FREQ_CW 20
#define INS_FREQ_CFR 25
#define INS_FREQ_ACR 29
#define INS_FREQ_POW 33
// For PHASE/PHASE2 sweep
#define INS_PHASE_POW 2
#define INS_PHASE_LSRR 5
#define INS_PHASE_RDW 8
#define INS_PHASE_FDW 13
#define INS_PHASE_CW 18
#define INS_PHASE_CFR 23
#define INS_PHASE_FTW 27
#define INS_PHASE_ACR 32

typedef struct ad9959_config {
    double ref_clk;
    uint32_t pll_mult;
    int sweep_type;
    uint channels;
    uint mirror;
} ad9959_config;

// get tuning words
double get_asf(double amp, uint16_t* asf);
double get_ftw(ad9959_config* c, double freq, uint32_t* ftw);
double get_pow(double phase, uint16_t* pow);
double get_time(ad9959_config* c, double time, uint32_t* cycles);

void load_acr(uint16_t asf, uint8_t* buf);
void load_ftw(uint32_t ftw, uint8_t* buf);
void load_pow(uint16_t pow, uint8_t* buf);

// send tuning words
void send_channel(uint8_t reg, uint8_t channel, uint8_t* buf, size_t len);
void send(uint8_t reg, uint8_t* buf, size_t len);

// Readback from AD9959
void read_reg(uint8_t reg, size_t len, uint8_t* buf);
void read_all();

// control
void set_pll_mult(ad9959_config* c, uint mult);
void set_ref_clk(ad9959_config* c, uint64_t freq);
void single_step_mode();
void clear();

// Sweep rate algorithm
double approx_double_32(double f, uint32_t * numerator, uint * denominator, uint32_t p_max, uint32_t q_max);
double approx_double_16(double f, uint16_t * numerator, uint * denominator, uint16_t p_max, uint16_t q_max);

#endif

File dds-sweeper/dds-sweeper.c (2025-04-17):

/*
#######################################################################
#                                                                     #
# dds-sweeper.c                                                       #
#                                                                     #
# Copyright 2023, Ethan Huegler                                       #
#                                                                     #
# Serial communication code based on the PineBlaster and PrawnBlaster #
#   https://github.com/labscript-suite/pineblaster                    #
#   Copyright 2013, Christopher Billington                            #
#   https://github.com/labscript-suite/prawnblaster                   #
#   Copyright 2013, Philip Starkey                                    #
#                                                                     #
# This file is used to flash a Raspberry Pi Pico microcontroller      #
# prototyping board to create a DDS-Sweeper (see readme.txt           #
# This file is licensed under the BSD-2-Clause license.               #
# See the license.txt file for the full license.                      #
#                                                                     #
#######################################################################
*/

#include <string.h>

#include "fast_serial.h"

#include "ad9959.h"
#include "hardware/clocks.h"
#include "hardware/dma.h"
#include "hardware/flash.h"
#include "hardware/pio.h"
#include "hardware/spi.h"
#include "pico/bootrom.h"
#include "pico/multicore.h"
#include "pico/stdlib.h"
#include "trigger_timer.pio.h"
#define VERSION "0.4.0"

// Mutex for status
static mutex_t status_mutex;
static mutex_t wait_mutex;

#define FLASH_TARGET_OFFSET (256 * 1024)

// STATUS flag
#define STOPPED 0
#define TRANSITION_TO_RUNNING 1
#define RUNNING 2
#define ABORTING 3
#define ABORTED 4
#define TRANSITION_TO_STOPPED 5
int status = STOPPED;

// modes
#define UNDEF_MODE -1
#define SS_MODE 0
#define AMP_MODE 1
#define FREQ_MODE 2
#define PHASE_MODE 3
#define AMP2_MODE 4
#define FREQ2_MODE 5
#define PHASE2_MODE 6

// clock status
#define INTERNAL 0
#define EXTERNAL 1
int clk_mode = INTERNAL;

// PIO VALUES IT IS LOOKING FOR
#define UPDATE 0


#define MAX_SIZE SWEEPER_MAX_SIZE // defined in CMakeLists.txt
#define TIMERS 5000
#define TIMING_OFFSET (MAX_SIZE - TIMERS * 4)

// minimum wait lengths
#define WAITS_SS_PER 250
#define WAITS_SS_BASE (500 - WAITS_SS_PER)
#define WAITS_SW_PER 500
#define WAITS_SW_BASE (1000 - WAITS_SW_PER)

// For responding OK to successful commands
#define OK() fast_serial_printf("ok\n")

// =============================================================================
// global variables
// =============================================================================
ad9959_config ad9959;
#define READSTRING_SIZE 256
char readstring[READSTRING_SIZE];
bool DEBUG = true;
bool timing = false;

uint triggers;

uint timer_dma;

uint INS_SIZE = 0;
uint8_t instructions[MAX_SIZE];
uint stop_ins = 0; // stop/repeat being unset denoted by 0

// bytes to encode an instruction in terms of sweep type
// order is single step, amp, freq, phase, amp2, freq2, phase2
uint BYTES_PER_INS[] = {8, 7, 13, 7, 13, 17, 13};

// instruction sizes after backend processing
// order is single step, amp, freq, phase, amp2, freq2, phase2
uint SIZE_EACH_INS[] = {14, 28, 29, 27, 36, 36, 36};

// =============================================================================
// Utility Functions
// =============================================================================

void init_pin(uint pin) {
    gpio_init(pin);
    gpio_set_dir(pin, GPIO_OUT);
    gpio_put(pin, 0);
}

void init_pio() {
    pio_clear_instruction_memory(PIO_TRIG);
    uint offset = pio_add_program(PIO_TRIG, &trigger_program);
    uint trigger = timing ? INT_TRIGGER : TRIGGER;
    uint profile_low = PROFILE_ASC ? P0 : P3;
    trigger_program_init(PIO_TRIG, 0, offset, trigger, profile_low, PIN_UPDATE);

    if(timing) {
        pio_clear_instruction_memory(PIO_TIME);
        offset = pio_add_program(PIO_TIME, &timer_program);
        timer_program_init(PIO_TIME, 0, offset, TRIGGER, INT_TRIGGER);
    }
}

int get_status() {
    mutex_enter_blocking(&status_mutex);
    int temp = status;
    mutex_exit(&status_mutex);
    return temp;
}

void set_status(int new_status) {
    mutex_enter_blocking(&status_mutex);
    status = new_status;
    mutex_exit(&status_mutex);
}

void measure_freqs(void) {
    // From https://github.com/raspberrypi/pico-examples under BSD-3-Clause License
    uint f_pll_sys = frequency_count_khz(CLOCKS_FC0_SRC_VALUE_PLL_SYS_CLKSRC_PRIMARY);
    uint f_pll_usb = frequency_count_khz(CLOCKS_FC0_SRC_VALUE_PLL_USB_CLKSRC_PRIMARY);
    uint f_rosc = frequency_count_khz(CLOCKS_FC0_SRC_VALUE_ROSC_CLKSRC);
    uint f_clk_sys = frequency_count_khz(CLOCKS_FC0_SRC_VALUE_CLK_SYS);
    uint f_clk_peri = frequency_count_khz(CLOCKS_FC0_SRC_VALUE_CLK_PERI);
    uint f_clk_usb = frequency_count_khz(CLOCKS_FC0_SRC_VALUE_CLK_USB);
    uint f_clk_adc = frequency_count_khz(CLOCKS_FC0_SRC_VALUE_CLK_ADC);
#ifdef CLOCKS_FC0_SRC_VALUE_CLK_RTC
    uint f_clk_rtc = frequency_count_khz(CLOCKS_FC0_SRC_VALUE_CLK_RTC);
#endif

    fast_serial_printf("pll_sys = %dkHz\n", f_pll_sys);
    fast_serial_printf("pll_usb = %dkHz\n", f_pll_usb);
    fast_serial_printf("rosc = %dkHz\n", f_rosc);
    fast_serial_printf("clk_sys = %dkHz\n", f_clk_sys);
    fast_serial_printf("clk_peri = %dkHz\n", f_clk_peri);
    fast_serial_printf("clk_usb = %dkHz\n", f_clk_usb);
    fast_serial_printf("clk_adc = %dkHz\n", f_clk_adc);
#ifdef CLOCKS_FC0_SRC_VALUE_CLK_RTC
    fast_serial_printf("clk_rtc = %dkHz\n", f_clk_rtc);
#endif
}

void update() { pio_sm_put(PIO_TRIG, 0, UPDATE); }

void sync() {
    gpio_put(PIN_SYNC, 1);
    sleep_ms(1);
    gpio_put(PIN_SYNC, 0);
    sleep_ms(1);
}

void reset() {
    gpio_put(PIN_RESET, 1);
    sleep_ms(1);
    gpio_put(PIN_RESET, 0);
    sleep_ms(1);

    sync();
    ad9959.sweep_type = 1;
    ad9959.channels = 1;
    ad9959.mirror = 0;
    INS_SIZE = 14;

    set_pll_mult(&ad9959, ad9959.pll_mult);

    clear();
    update();
}

void wait(uint channel) {
    pio_sm_get_blocking(PIO_TRIG, 0);
    triggers++;
}

void abort_run() {
    int local_status = get_status();
    if (local_status == RUNNING || local_status == TRANSITION_TO_RUNNING) {
        set_status(ABORTING);

        // Make trigger PIO trigger immediately so background aborts
        pio_sm_exec(PIO_TRIG, 0, pio_encode_push(false, false));

        // reinit PIO
        init_pio();
    }
}

// =============================================================================
// Set Table Instructions
// =============================================================================

void set_time(uint32_t addr, uint32_t cycles, int sweep_type, uint channels) {

    if (sweep_type == SS_MODE) {
        // single stepping
        if (cycles < WAITS_SS_BASE + WAITS_SS_PER * channels) {
            cycles = WAITS_SS_BASE + WAITS_SS_PER * channels;
        }
    } else {
        // sweeping
        if (cycles < WAITS_SW_BASE + WAITS_SW_PER * channels) {
            cycles = WAITS_SW_BASE + WAITS_SW_PER * channels;
        }
    }

    if (addr == 0) {
        // the first time through pio takes longer
        cycles -= 18;
    } else {
        cycles -= 10;
    }
    *((uint32_t *)(instructions + TIMING_OFFSET + 4 * addr)) = cycles;
}

/* offset from the beginning of this step to where this channel's instruction goes
*/
uint get_channel_offset(uint channel) {
    return INS_SIZE * channel + 1;
}

int get_offset(uint channel, uint addr) {
    // add one at the end here for this steps profile pin byte
    uint offset = (INS_SIZE * ad9959.channels + 1) * addr;

    // Space needed for timers
    uint tspace = timing ? TIMERS * 4 : 0;

    if (offset + get_channel_offset(channel) + INS_SIZE + tspace >= MAX_SIZE || (timing && addr > TIMERS)) {
        return -1;
    }

    return offset;
}

bool set_repeat_instruction(uint addr){
    int offset = get_offset(0, addr);
    if (offset < 0) {
        return false;
    }
    instructions[offset] = 0x00;
    instructions[offset+1] = 0xff;
    stop_ins = addr;  // update stop instruction
    return true;
}

bool set_stop_instruction(uint addr){
    int offset = get_offset(0, addr);
    if (offset < 0) {
        return false;
    }
    instructions[offset] = 0x00;
    instructions[offset+1] = 0x00;
    stop_ins = addr;  // update stop instruction
    return true;
}

void stop_ins_check(uint addr){
    // check if instruction overwrites the current stop instruction
    if (stop_ins != 0 && stop_ins == addr){
        // reset cached stop instruction address
        stop_ins = 0;
    }
}

void set_ins_csr(uint8_t * ins, uint channel){
    // set csr
    ins[INS_CSR] = AD9959_REG_CSR;
    if (ad9959.mirror) {
        ins[INS_CSR+1] = 0xf2;
    } else {
        ins[INS_CSR+1] = (1u << (channel + 4)) | 0x02;
    }
}

void set_ins_sweeps(uint addr, uint channel, bool rising){
    uint offset = get_offset(0, addr);
    // Profile pins are the same for all sweep types
    // Profile pins get updated twice for each trigger
    // the first update puts the profile pin high no matter what
    // then only if it is a downward sweep drop the profile pin low

    // The profile pin directions for a single table step are stored in a single byte
    // The least significant 4 bits in the byte correspond to the first value the
    // profile pin hits during an update. Since the pin should always go high first,
    // that means the least significant nibble should always be 0xf.
    if (rising && ad9959.mirror) {
        // case: upward sweep single channel mode
        instructions[offset] = 0xff;
    } else if (rising) {
        // case: upward sweep on this channel
        if (PROFILE_ASC) {
            instructions[offset] |= (1u << channel) | (1u << (channel + 4));
        }
        else {
            instructions[offset] |= (1u << (3 - channel)) | (1u << (7 - channel));
        }
    } else if (ad9959.mirror) {
        // case: downward sweep single channel mode
        instructions[offset] = 0x0f;
    } else {
        // case: downward sweep on this channel
        if (PROFILE_ASC) {
            instructions[offset] &= ~(1u << (channel + 4));
            instructions[offset] |= 1u << channel;
        }
        else {
            instructions[offset] &= ~(1u << (7 - channel));
            instructions[offset] |= 1u << (3 - channel);
        }
    }
}

/*
  Set single step instruction at offset for channel with
  Frequency Tuning Word
  Phase Offset Word
  Amplitude Control Register
 */
void set_single_step_ins(uint addr, uint channel,
                         uint32_t ftw, uint16_t pow, uint16_t asf){
    uint8_t ins[14];
    set_ins_csr(ins, channel);

    // Memory Map (12 bytes)
    // [ 0x00, CSR                      *Channel Select Register
    //   0x04, FTW3, FTW2, FTW1, FTW0,  *Frequency Tuning Word
    //   0x05, POW1, POW0,              *Phase Offset Word
    //   0x06, ACR2, ACR1, ACR0         *Amplitude Control Register
    // ]

    ins[INS_SS_FTW] = AD9959_REG_FTW;
    ins[INS_SS_POW] = AD9959_REG_POW;
    ins[INS_SS_ACR] = AD9959_REG_ACR;

    // profile pins do not matter for single tone mode, but the pio program
    // still expects a nonzero value for the profile pin mask
    instructions[get_offset(0, addr)] |= 0x01;

    load_acr(asf, &(ins[INS_SS_ACR+1]));
    load_ftw(ftw, &(ins[INS_SS_FTW+1]));
    load_pow(pow, &(ins[INS_SS_POW+1]));

    memcpy(instructions + get_offset(channel, addr) + get_channel_offset(channel), ins, INS_SIZE);
}
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

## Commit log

2022-06-28 tighten up timing on sweep examples
2022-07-12 profile pin masking
2022-07-27 found a similar arduino project
2023-01-09 removed debug printing
2023-01-17 added kicad files to project directory
    [dds-sweeper-board-Edge_Cuts.gbr, dds-sweeper-board-F_Cu.gbr, dds-sweeper-board.kicad_pcb, dds-sweeper-board.kicad_sch]
2023-01-17 board updates
    [dds-sweeper-board-Edge_Cuts.gbr, dds-sweeper-board-F_Cu.gbr, dds-sweeper-board-NPTH.drl, dds-sweeper-board-PTH.drl]
2023-01-17 removed backups from repo
    [dds-sweeper-board-Edge_Cuts.gbr, dds-sweeper-board-F_Cu.gbr, dds-sweeper-board-NPTH.drl, dds-sweeper-board-PTH.drl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]
2023-01-17 added manufacturing files
    [dds-sweeper-board-Edge_Cuts.gbr, dds-sweeper-board-F_Cu.gbr, dds-sweeper-board-NPTH.drl, dds-sweeper-board-PTH.drl]
2023-01-18 updated board desings
    [dds-sweeper-board-Edge_Cuts.gbr, dds-sweeper-board-F_Cu.gbr, dds-sweeper-board-NPTH.drl, dds-sweeper-board-PTH.drl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]
2023-01-18 only track gerber files for the board design
2023-01-19 added trigger input
    [dds-sweeper-board-Edge_Cuts.gbr, dds-sweeper-board-F_Cu.gbr, dds-sweeper-board-job.gbrjob]
2023-01-24 fixed print debug statements
2023-01-25 updated board files
    [dds-sweeper-board-Edge_Cuts.gbr, dds-sweeper-board-F_Cu.gbr, dds-sweeper-board-NPTH.drl, dds-sweeper-board-PTH.drl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]
2023-02-01 printed source to pdf
2023-02-08 added last printed files
2023-02-24 labeled schematic
    [dds-sweeper-board-Edge_Cuts.gbr, dds-sweeper-board-F_Cu.gbr, dds-sweeper-board-NPTH.drl, dds-sweeper-board-PTH.drl]
2023-03-03 increased trace width and spacing
    [dds-sweeper-board-Edge_Cuts.gbr, dds-sweeper-board-F_Cu.gbr, dds-sweeper-board-NPTH.drl, dds-sweeper-board-PTH.drl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]
2023-03-03 fixed board traces and keep outs
    [dds-sweeper-board-Edge_Cuts.gbr, dds-sweeper-board-F_Cu.gbr, dds-sweeper-board-NPTH.drl, dds-sweeper-board-PTH.drl]
2023-03-08 removed hard coded trigger pin from pio instructinos
2023-04-07 hit reset pin on software reset
2023-04-07 added test case to readme
2023-04-19 bigger traces
    [dds-sweeper-board-Edge_Cuts.gbr, dds-sweeper-board-F_Cu.gbr, dds-sweeper-board-NPTH.drl, dds-sweeper-board-PTH.drl]
2023-04-19 turned off input buffer on trigger pin
2023-08-22 Unzip KiCAD project, track individual files.
    Also updates project to KiCAD 7.0, made some minor tweaks to layout
    and schematic.
    [dds-sweeper-board-B_Cu.gbr, dds-sweeper-board-Edge_Cuts.gbr, dds-sweeper-board-F_Cu.gbr, dds-sweeper-board-NPTH.drl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]
2024-10-07 Fix remaining `printf` in ad9959.c
2024-10-07 Update testing notebook to actually run with current firmware (ie return strings only have `\n` now, not `\r\n`)
2024-10-26 Improve pin assignment flexibility: parameterize SPI, add option for ascending profile pins
2024-10-29 Updated board design
    [dds-sweeper-board-B_Cu.gbr, dds-sweeper-board-Edge_Cuts.gbr, dds-sweeper-board-F_Cu.gbr, dds-sweeper-board-NPTH.drl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]
2024-11-11 Added integer set command, removed debugging print
2025-02-07 Fix incorrect byte extraction from setb amplitude sweep loading. Removed extraneous print.
2025-02-18 Add `clkstatus` command to get current clock configuration of the DDS sweeper.
2025-02-26 added some handling for the readtable byte blocks to put in a header and pipe separators, currently looks ugly but its to make debugging easier (potentially)
2025-03-11 cut down the function to be less memory hungry, favored fast_serial_printf over sprints for concats. This all works on this branch.
2025-03-13 Expand possible status states to be finer grained, and more closely match labscript device statuses
2025-03-21 Initial framework for tracking the stop command.
    Commit contains debug print, has not replaced for-loop calcs,
    and does not protect against running tables without a stop yet.
2025-03-21 Clean up superfluous debug prints.
    Debug now only reports rounding of settings.
2025-03-21 fix swap in multiply vs divide logic in get_time and used g format for float printing
2025-03-24 FROM/as case mismatch
2025-03-24 switch to camel case for correct function call
2025-04-03 semi-implemented modified continued fraction alg, debugging currently, saving progress
2025-04-04 an idea, why not have the falling case just use the same function but enforce the denominator to be 1? I believe thats the same as before, but outskirts the bounds on get_asf()
2025-04-17 Document `board` command and change its response slightly.
